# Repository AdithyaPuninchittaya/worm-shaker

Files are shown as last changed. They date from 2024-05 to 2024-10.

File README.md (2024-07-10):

## The full research paper for this project which details the rationale, methods, results, and discussion is linked here: [https://docs.google.com/document/d/1LjSq2D_FG7MaTCYWkhqbbYRr-aXNf1JoYAtKsyUWb9E/edit?usp=sharing](https://docs.google.com/document/d/1LjSq2D_FG7MaTCYWkhqbbYRr-aXNf1JoYAtKsyUWb9E/edit?usp=sharing). The relevant Materials and Methods section is listed below as a reference. 

## Design of Assembly
The habituation device was designed using Fusion 360 as a multi-part file on a PC. As shown in Figure 1, the bottom case houses the Seeed Studio XIAO SAMD21 microcontroller, with an opening for the USB-C combined data and power port. The bottom case has holes so that the entire *C. elegans* plate can be viewed under a bottom-lit stereo zoom microscope. 

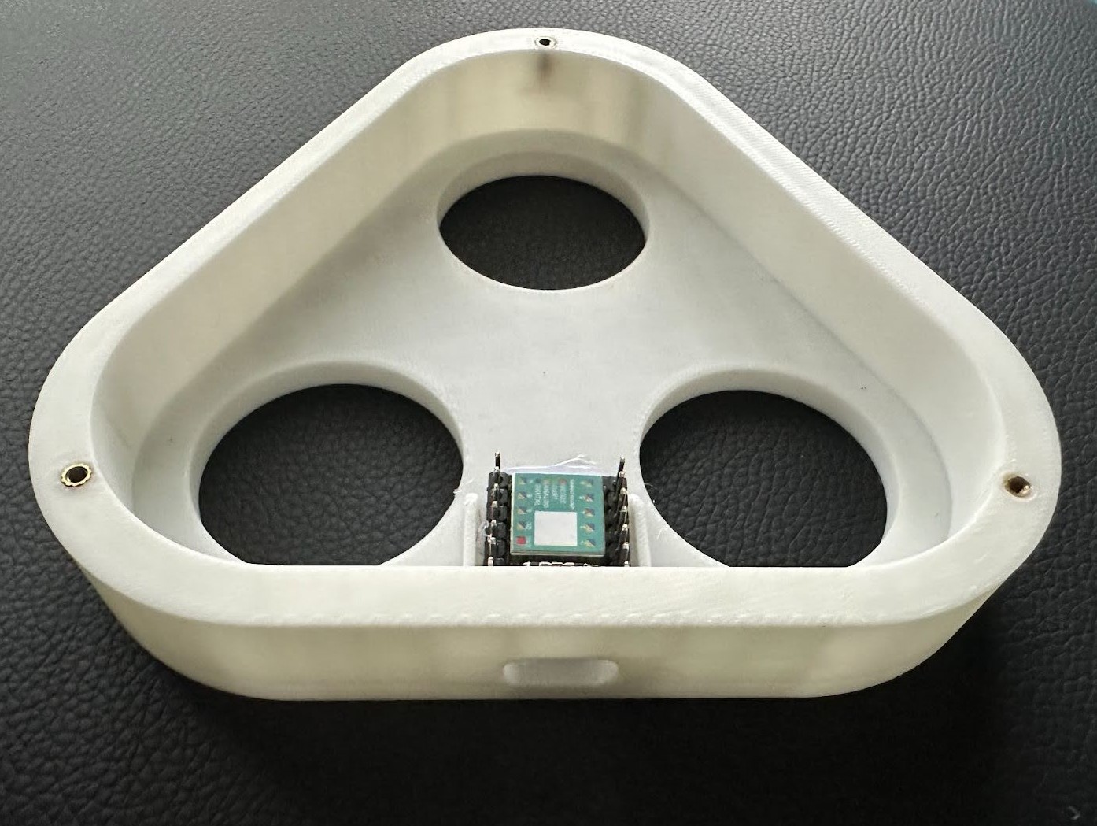
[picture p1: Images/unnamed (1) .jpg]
Figure 1: Image showing the bottom case of the habituation device.
|  |
|:--:| 
| *Figure 1: Image showing the bottom case of the habituation device.* |

The top plate, as shown in Figure 2 below, is designed to simultaneously accommodate three 35 mm bacteriological Petri dishes in a triangular configuration. The top plate also has mounting points for the three vibration motors (Garosa Vibration Motor 11500rpm) placed equidistantly between the Petri dish holders. The motors were placed so that each was tangent to the two adjacent Petri dishes, ensuring an even distribution of vibrational stimuli. 

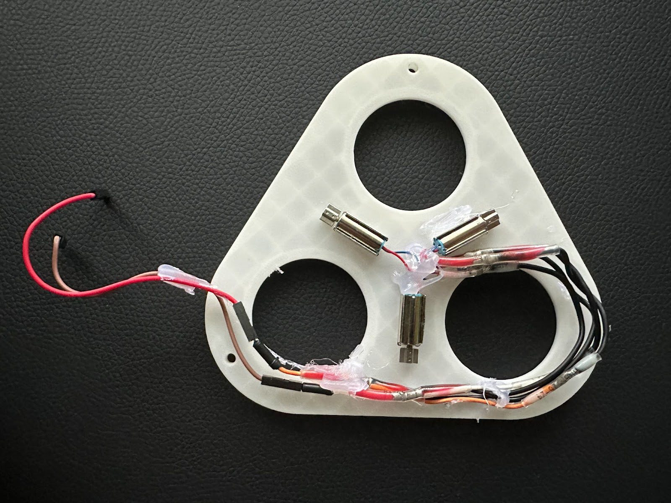
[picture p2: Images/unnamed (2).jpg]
Figure 2: Image showing the top plate and the associated wiring harness.
|  |
|:--:| 
| *Figure 2: Image showing the top plate and the associated wiring harness.* |

The STL files for the design are found in the GitHub repository linked here: [https://github.com/AdithyaPuninchittaya/worm-shaker](https://github.com/AdithyaPuninchittaya/worm-shaker).

## Fabrication of Assembly  
The STL files were sliced using Bambu Studio and then transferred to the Bambu Lab X1C printer, where the models were printed using Bambu PLA Basic filament. Once printing was completed, the printed parts were carefully removed from the print bed. Support materials were removed for smooth assembly. Heated inserts were installed in the designated holes for mounting components. The inserts were heated using a soldering iron and then pressed into the holes to create strong and threaded connections for screws.

A wiring harness was created to connect the vibration motors to the Seeed Studio XIAO SAMD21 microcontroller, as shown, using spare jumper wires. Wires from the motors were then routed against the device frame and hot-glued in place to the top plate. The wiring diagram is shown below in Figure 3. 

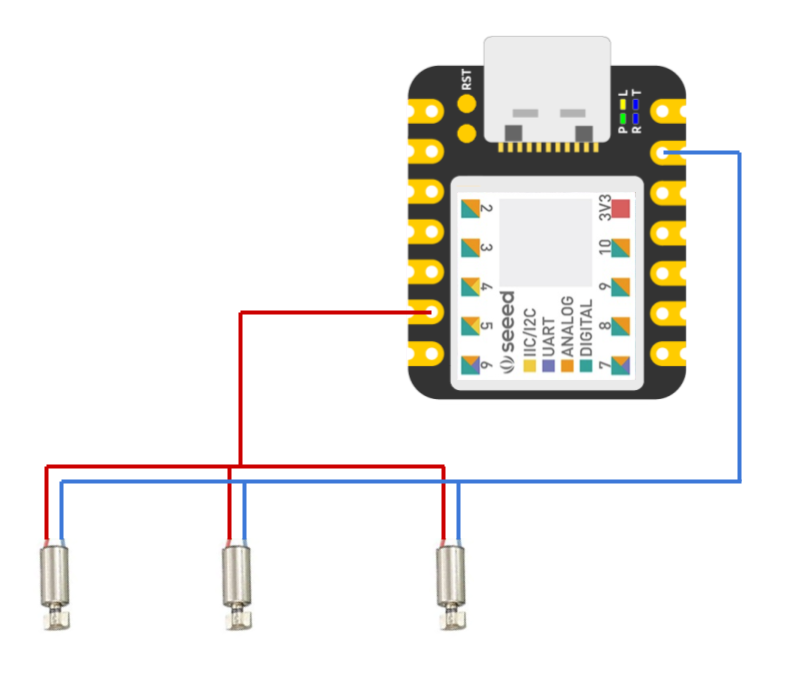
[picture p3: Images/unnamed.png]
Figure 3: Image showing the wiring diagram for the wiring harness.
|  |
|:--:| 
| *Figure 3: Image showing the wiring diagram for the wiring harness. * |

## Programming
The Arduino Integrated Development Environment (IDE) was installed on a computer. The necessary library for the Seeed Studio XIAO SAMD21 was installed. The microcontroller was connected to the laptop via USB-C, and the board settings in the Arduino IDE were configured to match the analog port of the Seeed Studio XIAO SAMD21. A custom program was written to control the vibration sequence. The program included variables for vibration duration, intensity, and inter-stimulus interval. The program's main loop sends signals to the analog port, which activates the motors according to the specified parameters. The code can be found below in Figure 4 and in the GitHub repository linked here: [https://github.com/AdithyaPuninchittaya/worm-shaker/wormshaker.ino](https://github.com/AdithyaPuninchittaya/worm-shaker/wormshaker.ino). The program and vibration cycle runs when the device is powered via a USB-C cable. 

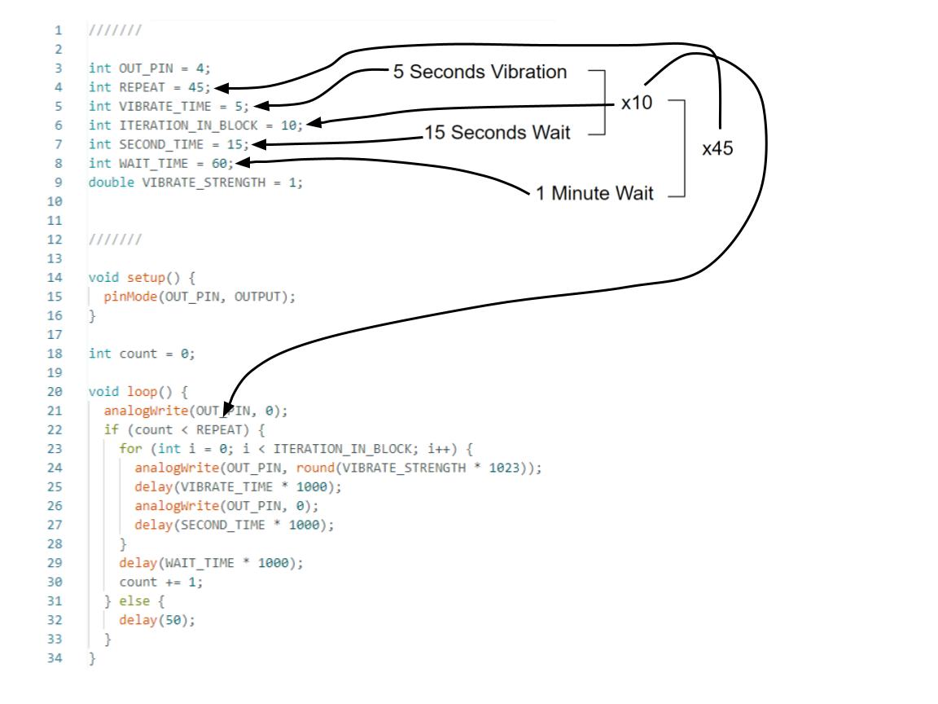
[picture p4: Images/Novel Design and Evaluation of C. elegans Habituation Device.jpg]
Figure 4: Image showing example code that the microcontroller runs and a diagram of its cycle.
|  |
|:--:| 
| *Figure 4: Image showing example code that the microcontroller runs and a diagram of its cycle.* |

## Bill of Materials

| Item Name | Link | Unit Cost ($) | Quantity | Total Cost ($) |
|-----------|------|---------------|----------|----------------|
| M3 Screws 10mm (100 pack of screws) | [Amazon](http://amazon.com/Mxfans-100pcs-Carbon-Countersunk-Socket/dp/B07DWVDDWC) | 0.062 | 3 | 0.186 |
| Optional Rubber Washers (for dampening between plates) | [Amazon](http://www.amazon.com/uxcell-Gasket-Rubber-Washer-Grommet/dp/B01MTDD2R9) | 0.3 | 3 | 0.9 |
| Heatset Inserts | [Amazon](http://amazon.com/uxcell-Knurled-Insert-Female-Embedding) | 0.07575 | 3 | 0.22725 |
| XIAO SAMD21 | [Amazon](https://www.amazon.com/Seeeduino-Smallest-Microcontroller-Interfaces-Compatible/dp/B08745JBRP) | 8.33 | 1 | 8.33 |
| Male to Male Jumper Wires | [Amazon](https://www.amazon.com/Seeeduino-Smallest-Microcontroller-Interfaces-Compatible/dp/B08745JBRP) | 0.999 | 5 | 4.995 |
| Vibration Motors | [Amazon](https://www.amazon.com/11500rpm-Vibration-Vibrating-Detection-Equipment/dp/B087XCFCLL) | 2.094 | 3 | 6.282 |
| Top Plate (STL File) | [Print File](https://github.com/AdithyaPuninchittaya/worm-shaker/blob/main/Print%20Files/Top%20Plate.stl) | 0.60 | 1 | 0.60 |
| Bottom Case (STL File) | [Print File](https://github.com/AdithyaPuninchittaya/worm-shaker/blob/main/Print%20Files/Bottom%20Case.stl) | 1.07 | 1 | 1.07 |
| **Total Cost** | | | | **22.60** |

# RESULTS

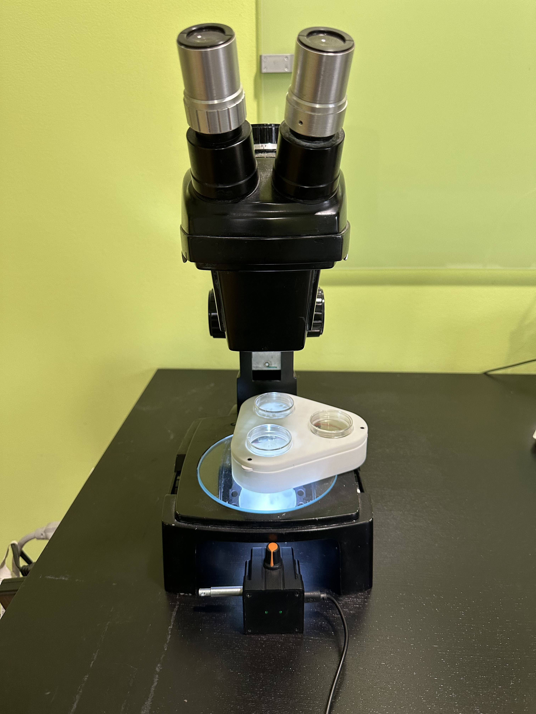
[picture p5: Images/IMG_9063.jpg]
Figure 5: Final design and assembly of the habituation device, housing three 35 mm *C. elegans* plates
|  |
|:--:| 
| *Figure 5: Final design and assembly of the habituation device, housing three 35 mm C. elegans plates * |

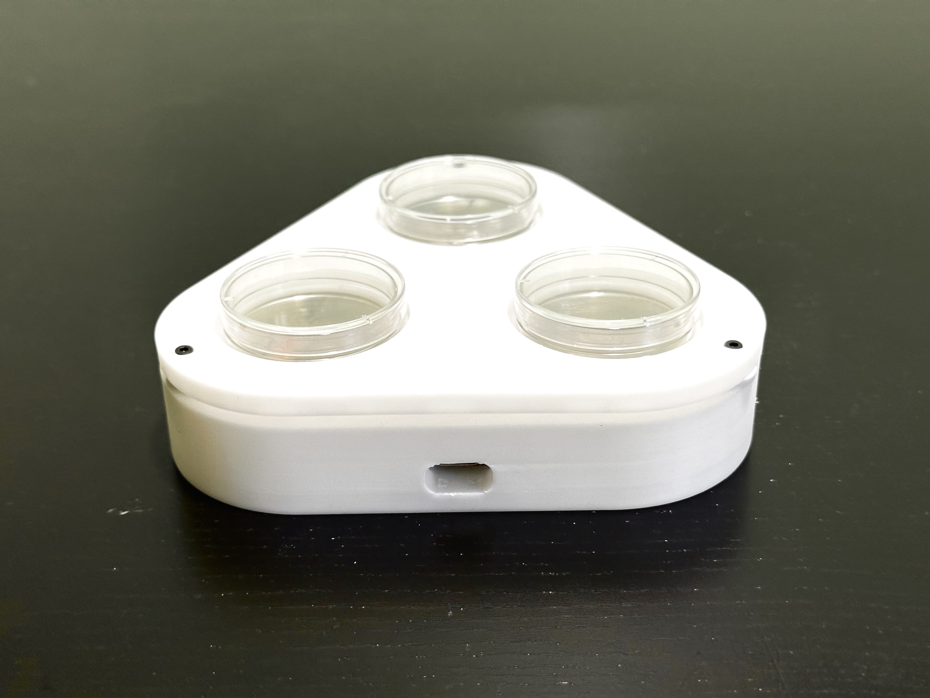
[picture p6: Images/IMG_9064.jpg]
Figure 6: Image of habituation device on microscope setup for recording.
|  |
|:--:| 
| *Figure 6: Image of habituation device on microscope setup for recording.* |

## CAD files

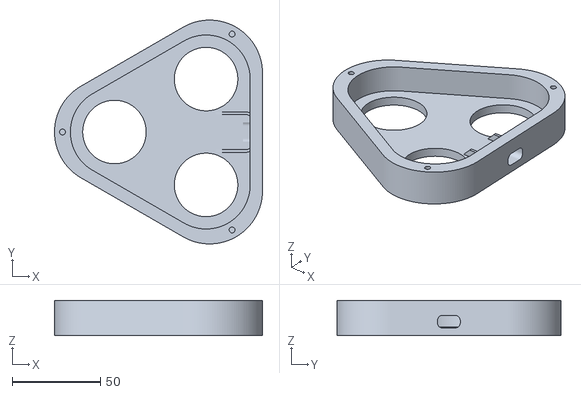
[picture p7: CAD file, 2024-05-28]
Print Files/Bottom Case.stl
118.0 x 126.9 x 20.0

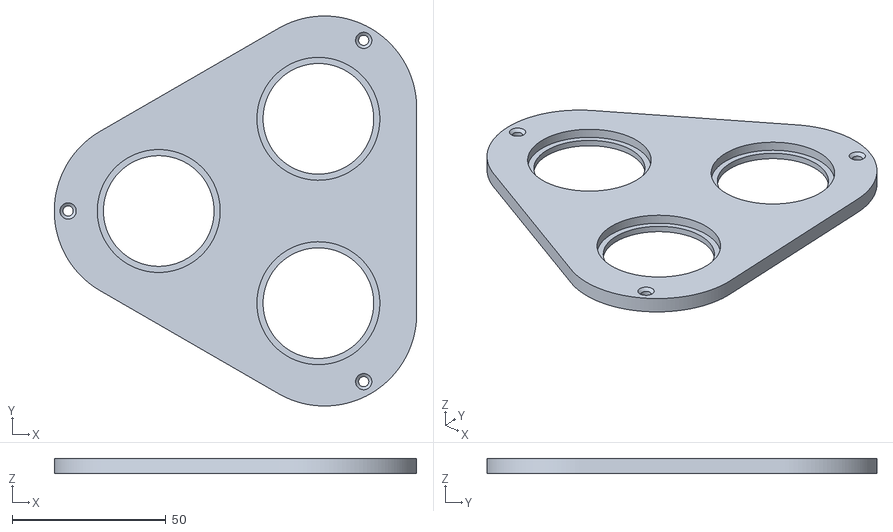
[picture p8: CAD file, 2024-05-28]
Print Files/Top Plate.stl
118.0 x 126.9 x 5.00

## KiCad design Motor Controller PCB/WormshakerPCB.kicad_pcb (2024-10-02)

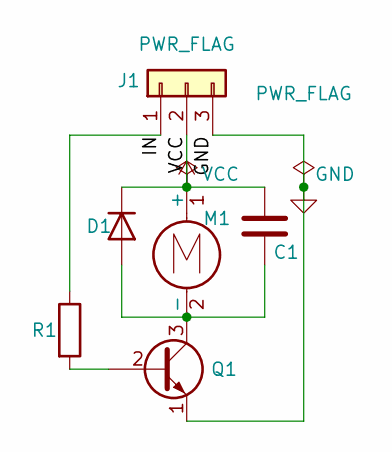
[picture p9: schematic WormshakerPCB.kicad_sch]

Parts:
C1: C; C_Disc_D5.1mm_W3.2mm_P5.00mm
D1: 1N4001; D_DO-41_SOD81_P10.16mm_Horizontal
J1: Conn_01x03; PinHeader_1x03_P2.54mm_Vertical
M1: Motor_DC; PinHeader_1x02_P2.54mm_Vertical
Q1: 2N2219; TO-92L_Inline
R1: R; R_Axial_DIN0207_L6.3mm_D2.5mm_P7.62mm_Horizontal

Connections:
/IN: J1.1, R1.1
GND: J1.3, Q1.1 (E)
unnamed: C1.2, D1.2 (A), M1.2 (-), Q1.3 (C)
unnamed: Q1.2 (B), R1.2
VCC: C1.1, D1.1 (K), J1.2, M1.1 (+)

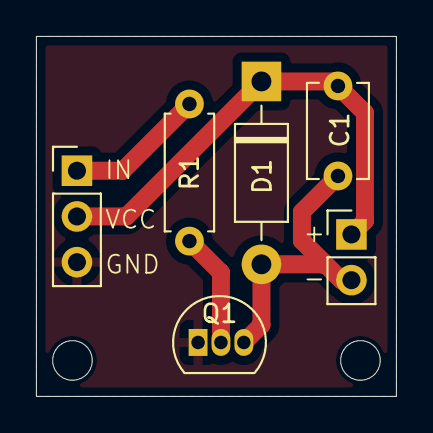
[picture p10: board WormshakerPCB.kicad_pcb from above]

Board: 2 copper layers, 20.0 x 20.0 mm, 8 parts (0 on the bottom side), 5 nets.

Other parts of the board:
REF1, REF2: MountingHole_2.2mm_M2_DIN965

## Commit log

2024-05-28 Add files via upload
    STL Files for 3D printing the bottom case and top plate of the Novel C. elegans Habituation Device
    [Bottom Case.stl, Top Plate.stl]
2024-05-28 Rename Bottom Case.stl to Print Files/Bottom Case.stl
    [Bottom Case.stl]
2024-05-28 Rename Top Plate.stl to Print Files/Top Plate.stl
    [Top Plate.stl]
